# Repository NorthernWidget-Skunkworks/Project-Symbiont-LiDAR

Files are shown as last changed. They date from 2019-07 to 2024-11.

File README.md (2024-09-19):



# Project-Symbiont-LiDAR
Design files for a support and interface unit for the Garmin LiDAR Lite

Symbiosis

***The symbiont.*** *Lichens, like this Reindeer Lichen found in northeastern
Minnesota, are a symbiosis between fungi and algae. Our symbiosis is between
silicon, copper, aluminum, and laser. But be it nature or machine, some
partnerships are truly mutual in their benefits. Photo by Homer Edward Price.*

The [LiDAR Lite](https://buy.garmin.com/en-US/US/p/578152/pn/010-01722-10) is a rangefinder from Garmin capable of returning distances to objects up to 40 m away. It is an effective sensor for water, snow, and ice levels, among other purposes. Extensive work to characterize the LiDAR Lite for environmental sensing of water levels has been performed by:

Paul, J. D., Buytaert, W., & Sah, N.(2020). A technical evaluation of lidar-based measurement of riverwater levels. *Water Resources Research*, *56*, e2019WR026810. https://doi.org/10.1029/2019WR026810

## Technical specifications

### Electronic Hardware

* Microcontroller (computer) core
  * ATTiny1634
  * [Firmware](Firmware) written in Arduino-compatible C++
  * 12 MHz
* Sensors
  * Externally connected: [Garmin LiDAR Lite v3 HP](https://buy.garmin.com/en-US/US/p/578152/pn/010-01722-10)
  * On board
    * MEMS accelerometer to detect board angle
    * Hall-effect sensor to for user to trigger with a magnet after providing a known angle to the accelerometer. This corrects for offset errors in the accelerometer, significantly improving its angular accuracy.
* Connections and communications protocols
  * [LiDAR Lite v3 HP](https://buy.garmin.com/en-US/US/p/578152/pn/010-01722-10)
    * 6-pin screw-terminal header
    * Switchable 5V power supply
    * I2C
  * Data logger
    * Power in and Ground
    * Digital communications
      * I2C
* Power
  * Voltage limits: 3.3 ~ 5.5V
  * Power consumption: ~0.5mA @ 4.5V, take reading every 60 seconds, then power down
  * Power conditioning: Provides an onboard, high power, step up to 5V to allow for interface to 3.3V loggers
* Fault recovery: Using intermediate system to emulate an I2C connection prevents a global lockup of the logger system
* Status LED
* Open-source licensing via CC BY-SA 4.0

Symbiont board

### Electronic Software and Firmware

* Programmable using the Arduino IDE https://www.arduino.cc/en/main/software
* [Firmware](Firmware) available in this repository. At the time of writing, "LiDAR_InterfaceDemo" is the most up-to-date prototype firmware.
* [Software ](https://github.com/NorthernWidget-Skunkworks/Symbiont-LiDAR_Library) to use the Symbiont-LiDAR with Arduino-compatible devices
* Open-source licensing via GNU GPL 3.0

## Assembly

Rendered image of assembled LiDAR unit

Assembling this sensor is possible by hand with sufficient skill and the following tools:
* Temperature-controlled soldering iron
* Hot-air rework station
* Equipment for stenciling with solder paste
* ESD-safe tweezers and workstation
* Solder wick

Most of the components on this board are coarse enough in pitch that assembly by hand is expected to be relatively straightforward. However, if you are concerned about this, there are PCB assembly workshops located in many parts of the world.
>> THOUGHT: I have basic instructions for assembly on the [Project Walrus](https://github.com/NorthernWidget-Skunkworks/Project-TPDH-Walrus) README; I will not reproduce these here just yet, as we might want to set up a separate assembly guide, mostly with good links to existing resources, since our writing something of this nature would be to reinvent the wheel.

## Firmware

### Downloading and installing the Arduino IDE

Go to https://www.arduino.cc/en/main/software. Choose the proper IDE version for your computer. For Windows, we suggest the non-app version to have more control over Arduino; this might change in the future. You will have to add custom libraries, so the web version will not work (at least, as of the time of writing). Download and install the Arduino IDE. Open it to begin the next steps.

### AVR ISP

To install firmware on the Symbiont board, you use the [2x3-pin 6-pin ICSP (also called ISP) header](https://www.digikey.com/product-detail/en/3m/929665-09-03-I/3M156313-06-ND/681796) with a special device called an "in-circuit system programmer" (or just "in-system programmer; yup, that's what the acronym stands for).

Many devices exist to upload firmware, including:
* The official [AVR ISP mkII](http://ww1.microchip.com/downloads/en/DeviceDoc/Atmel-42093-AVR-ISP-mkII_UserGuide.pdf) (no longer produced but available used)
* Using an [Arduino as an ISP](https://www.arduino.cc/en/tutorial/arduinoISP)
* The versatile [Olimex AVR-ISP-MK2](https://www.olimex.com/Products/AVR/Programmers/AVR-ISP-MK2/open-source-hardware)
* The [Adafruit USBtinyISP](https://www.adafruit.com/product/46)

### Uploading the firmware

Using this ISP, upload (as of the time of writing): [the Arduino sketch in this folder](Firmware/AdditionalFirmware/LiDAR_Accelerometer_InterfaceDemo). To do so, follow these steps:

1. Open the Arduino IDE.
2. Follow [these instructions](https://github.com/SpenceKonde/ATTinyCore/blob/master/Installation.md) to install the [ATTinyCore board definitions](https://github.com/SpenceKonde/ATTinyCore)
3. Select [ATTiny1634](https://github.com/SpenceKonde/ATTinyCore/blob/master/avr/extras/ATtiny_1634.md) **(No bootloader)**
4. Plug your ISP of choice into your computer (via a USB cable) and onto the 6-pin header. There are two ways to place it on; the header is aligned such that the ribbon cable should be facing away from the board while programming. If this fails without being able to upload, try flipping the header around. This should both power the board and provide communications.
5. Go to Tools --> Programmer and select the appropriate programmer based on what you are using.
6. Go to Tools --> Burn Bootloader. Yes, we know that you just selected "ATTiny1634 (No bootloader)", but this step sets the fuses, which configure their internal oscillator and brown-out detection.
7. Go to Sketch --> Upload Using Programmer. After several seconds, you learn whether you succeeded or failed. Hopefully it worked!

Upload using programmer

***Uploading using the in-system programmer.***

***Important note for Linux users:*** You must supply permissions to the Arduino IDE for it to be able to use the ICSP, or you will have to run it using `sudo`. The former option is better; the latter is easier in the moment.

***Note: Be sure to download and/or update drivers for your ISP.***

## Writing a program to connect to the Symbiont-LiDAR

Once it is bootloaded and connected with a LiDAR Lite sensor, you should be able to use any standard Arduino device to connect to it and read its data.

### Very simple Arduino code

This code is intended for any generic Arduino system.

```c++
// Include the Symbiont library
#include "SymbiontLiDAR.h"

// Declare variables -- just as strings
String header;
String data;

// Instantiate class
SymbiontLiDAR myLaser;

void setup(){
    // Begin Serial connection to computer at 38400 baud
    Serial.begin(38400);
    // Obtain the header just once
    header = myLaser.getHeader();
    // Print the header to the serial monitor
    Serial.println(header);
}

void loop(){
    // Take one reading every (10 + time to take reading) seconds
    // and print it to the screen
    myLaser.updateMeasurements();
    data = myLaser.getString();
    Serial.println(data);
    delay(10000); // Wait 10 seconds before the next reading, inefficiently
}
```

### Northern Widget Margay code

The [Margay data logger](github.com/NorthernWidget-Skunkworks/Project-Margay) is the lightweight and low-power open-source data-logging option from Northern Widget. It saves data to a local SD card and includes on-board status measurements and a low-drift real-time clock. We have written [a library to interface with the Margay](github.com/NorthernWidget-Skunkworks/Margay_Library), which can in turn be used to link the Margay with sensors.

```c++
// Include the Symbiont library
#include "Margay.h"
#include "SymbiontLiDAR.h"

// Declare variables -- just as strings
// Empty header to start; will include sensor labels and information
String header = "";
String data;

// Instantiate classes
SymbiontLiDAR myLaser;
Margay Logger; // Margay v2.2; UPDATE CODE TO INDICATE THIS

// I2CVals for Symbiont
uint8_t I2CVals[] = {0x50}; // DEFAULT

//Number of seconds between readings
uint32_t updateRate = 60;

void setup(){
    header = header + myLaser.getHeader();
    Logger.begin(I2CVals, sizeof(I2CVals), header);
    initialize();
}

void loop(){
    Logger.run(update, updateRate);
}

String update() {
    initialize();
    return myLaser.getString();
}

void initialize(){
    myLaser.begin();
}
```

### Northern Widget Resnik code

>> Currently nearly identical to Margay code, by design. Add telemetry with Particle Boron.

```c++
// Include the Symbiont library
#include "Resnik.h"
#include "SymbiontLiDAR.h"

// Declare variables -- just as strings
// Empty header to start; will include sensor labels and information
String header;
String data;

// Instantiate classes
SymbiontLiDAR myLaser;
Resnik Logger;

// I2CVals for Symbiont
uint8_t I2CVals[] = {0x50}; // DEFAULT

//Number of seconds between readings
uint32_t updateRate = 60;

void setup(){
    header = header + myLaser.getHeader();
    Logger.begin(I2CVals, sizeof(I2CVals), header);
    initialize();
}

void loop(){
    Logger.run(update, updateRate);
}

String update() {
    initialize();
    return myLaser.getString();
}

void initialize(){
    myLaser.begin();
}
```

## Housing and cabling

### Parts required

This is what we used for our build; you can be creative based on materials and availability.

* Main enclosure
  * Polycase box [WC-20F (clear lid)](https://www.polycase.com/wc-20f)
  * [2x \#4 screws](https://www.polycase.com/screws-mbr-100) to mount Symbiont in box
  * Cable gland ([Heyco M4365](https://www.heyco.com/Liquid_Tight_Cordgrips/product.cfm?product=Liquid-Tight-Cordgrips-Metric&section=Liquid_Tight_Cordgrips)) for cable to LiDAR Lite
  * Strain-relieved cable gland ([Heyco M4425](https://www.heyco.com/Liquid_Tight_Cordgrips/product.cfm?product=Liquid-Tight-Cordgrips-Pigtail-Metric&section=Liquid_Tight_Cordgrips)) for cable to logger
  * Desiccant packs
* LiDAR Rangefinder and attachment to enclosure
  * [LiDAR Lite sensor](https://www.sparkfun.com/products/14599)
  * [4 sealing screws](https://www.mcmaster.com/90825A144/): \#4-40 x 3/8"
  * [4 washers](https://www.mcmaster.com/90107A005) for \#4 screws
  * [4 cap nuts](https://www.mcmaster.com/99022A101) for \#4-40 screws
* Mounting plate
  * Material: Acetal (Delrin) sheet: 1/4" thick. We commmonly use [12x24" black](https://www.eplastics.com/ACTLBLK0-25012X24); the black pigment increases its UV resistance
  * Rectangular dimensions for mount: 127 x 95.25 x 6.35 mm (5.00" x 3.75" x 0.25")
  * [Design](https://easel.inventables.com/projects/VMmCoOyJyiiKTospk1NBBQ) on Easel for X-carve (see also [CNC files here](CNC)). Note the 7 mm depth to ensure that the bit cuts all the way through the Acetal; use a piece of scrap material on your cutting bed if you want to protect it.
* Mounting plate fasteners
  * 1/4"-20 hardware to attach the box to the mounting plate
    * Bolts: [1" long; hex head convenient; zinc-plated medium-grade (Grade 5) recommended for lower price with good corrosion resistance](https://www.mcmaster.com/92865A542)
    * Nuts: [Zinc-plated Grade 5](https://www.mcmaster.com/95462A029)
    * Washers: Zinc-plated [SAE](https://www.mcmaster.com/90126A029) or [USS](https://www.mcmaster.com/90108A413)
    * Lock washers: We typically use [split-lock washers](https://www.mcmaster.com/zinc-plated-steel-washers/), but [tooth-lock washers](https://www.mcmaster.com/91113A029) are good for high-vibration environments.
  * 2 U bolts: 1/4"-20, inner diameter 3/4" to 1 3/4", to attach the mounting plate to a pipe. We typically mount this sensor on 3/4" pipe or conduit, and recommend a U bolt designed to fit this ([1/4"-20, 1 1/8" inner diameter](https://www.mcmaster.com/u-bolts/u-bolts-with-mounting-plates/for-pipe-size~3-4/)). Weather/corrosion resistance is helpful, especially if you are concerned about later removing the U bolts.
* Cable to logger
  * 3 m (or less) [4-conductor AlphaWire](https://www.digikey.com/product-detail/en/alpha-wire/5004C-SL001/5004CSL001-ND/484976), stripped and tinned at both ends. Other cables will work too; this is what we have found to be highest quality and reliability. We cannot guarantee successful I<sup>2</sup>C communications over cables longer than 3 meters.

Mounting plate perspective view in Easel

***Mounting plate perspective view in [Easel](https://easel.inventables.com/projects/VMmCoOyJyiiKTospk1NBBQ)*** *for easy integration with the X-carve series of lower cost CNC routers.*

### Assembly

Prior to assembly, ensure that you have:
* [Uploaded the firmware to the Symbiont board](#Uploading-the-firmware)
* Fabricated [the mounting plate](CNC) (see also the [Easel online CNC setup](https://easel.inventables.com/projects/VMmCoOyJyiiKTospk1NBBQ)) if desired.

1. Drill and tap 12 mm holes in the side of the box. Use a M12-1.5 tap for the threads.

2. Install the Symbiont board as shown below using two of the \#4 self-tapping screws.

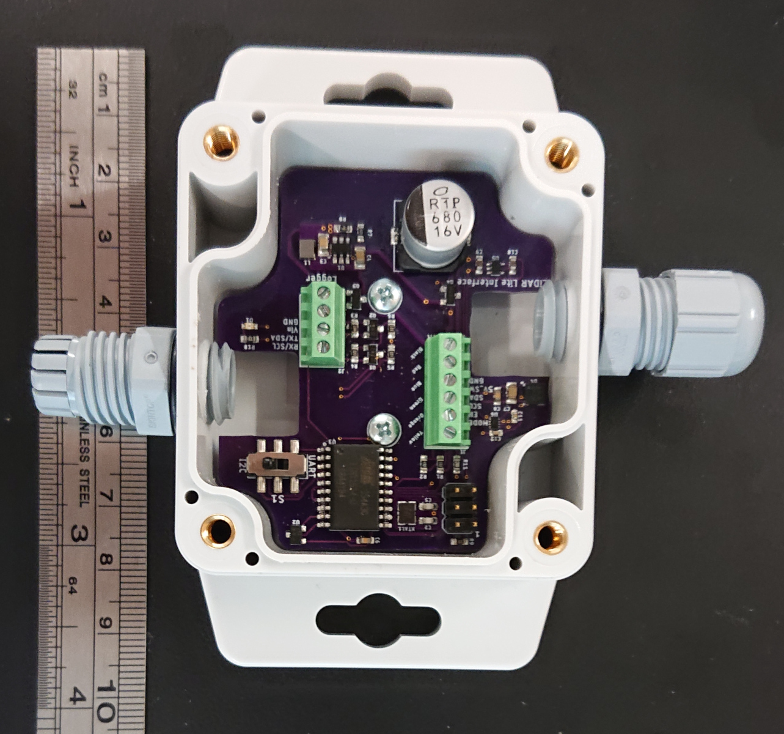
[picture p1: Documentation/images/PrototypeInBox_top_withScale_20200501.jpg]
Symbiont prototype in box


3. Using the sealing screws, cap nuts, and washers, install the LiDAR Lite sensor onto the lid. By mounting the LiDAR Lite at an angle, you can fix it to the box lid in a way that still allows the box to open and close properly. The cap nuts go on the outside of the housing.

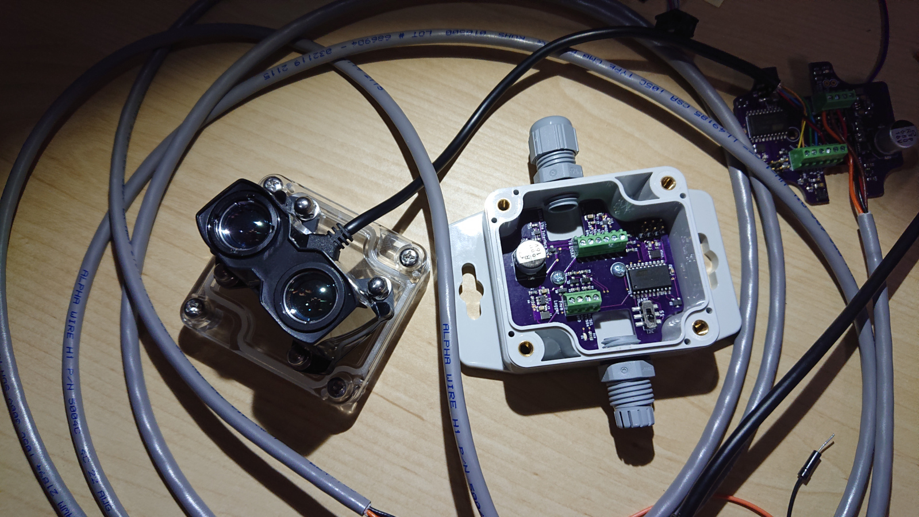
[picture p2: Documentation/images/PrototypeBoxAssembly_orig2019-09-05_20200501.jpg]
Prototype sensor assembly


4. Thread the cables through the cable glands and attach them to the screw terminals. A 1.8 mm flat-head screwdriver can be very useful for this. Note that these cables cross the board in the above image (upper left) -- and that (unlike in the image!) you should do this *after* the board is in the box.

5. Using the switch in the box, select the desired communications protocol. For most of our uses, this is I2C.

6. Attach the cable to the data logger.

7. Test the LiDAR Lite unit.

8. When satisfied with the tests, turn off the data logger and place a protective cover over the lenses of the LiDAR Lite for safety during transport. We have [a set of "safety glasses" available for 3D printing](3Dprint). You may want to secure these in place with electrical tape.

9. Place desiccant in the box. I typically install two small desiccant packs on the side of the board above the switch and large capacitor and pack them in so they are unlikely to move; this is in order to keep the indicator LED visible.

10. Securely screw the lid onto the box to seal the LiDAR Lite + Symbiont unit.

11. Mark the corner of the box next to the Hall-effect sensor, and mark the orientations of the roll and pitch axes. The pitch axis should be positive when the long strain-relieved cable gland tilts upwards. The roll axis should be positive when, when looking at the side of the assembly such that the long strain-relieved cable gland is on the left and the laser rangefinder is pointed up, the laser rangefinder rolls towards you.

Side view: long axis, with pitch +/- marked

Side view: short axis, LiDAR Lite cable, with roll +/- marked

>> Add an annotated picture of Hall-Effect sensor location

12. Place the box on a measured flat surface and tap the magnet to the marked location by the Hall Effect sensor. This will appropriately zero the offsets for the sensor and increase its near-horizontal accuracy significantly. This must be done when the sensor is powered; the LED will light up during the full duration of magnetic contact. When connected to a logger, this can be done by putting the magnet in place, hitting the "RESET" button (e.g., on a Margay logger), and then holding the magnet in place with the read light on until the first reading is complete. Doing this while connected to a computer is recommended in order to see the first reading on the serial monitor and double check that the zeroing/calibration is appropriate. For a convenient magnet holder, you can use our [3D-printable magnetic wand][3Dprint], which holds a small rare-Earth magnet. This may be a generic part, though this [3/8" x 1/8" Neodymium Disk Magnet](https://www.apexmagnets.com/magnets/3-8-x-1-8-disc-neodymium-magnet) works well in our experience.

13. Use the 1/4"-20 hardware to attach the LiDAR Lite box to the mounting plate. The bolts pass through the center holes on the tabs on either side of the box, with their heads towards the box lids.

>> Note: Mounting plate holes currently too small for these; will need to be updated. Currently using #8 hardware. Figures for pitch+roll have 1/4-20 -- I probably drilled it out wider for these.

14. (Can wait for field installation) attach the unit via its mounting plate to the appropriate pipe, post, etc. This typically involves the U bolts, noted above. Curved EMT conduit can be helpful for providing a way to select the angle of the sensor. Although we use a single 45-degree bend piece of conduit in the images below, we might suggest attaching a 90-degree bend conduit first, and then a 45-degree bend as necessary to adjust the sensor away from a direct down-looking view; the sensor will attach directly to the convex side of the bend instead of bridging over airspace, which required us to use rocks as shims to reduce mounting-plate flexure. (This suggestion, however, increases torque on the mast; future field testing is needed to determine the best method.) ***Note: The LiDAR Lite unit will likely give a return only if its angle to the surface that it is measuring is steeper (i.e., more orthogonal) than 45 degrees.***

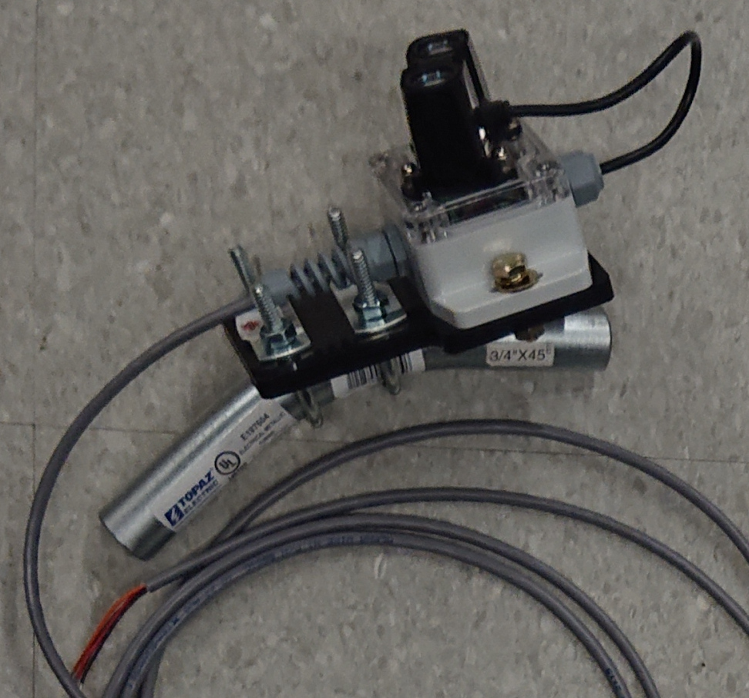
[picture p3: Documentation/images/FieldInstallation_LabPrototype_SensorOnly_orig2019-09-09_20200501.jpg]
Field installation prototype in the lab: Sensor only


## Field installation

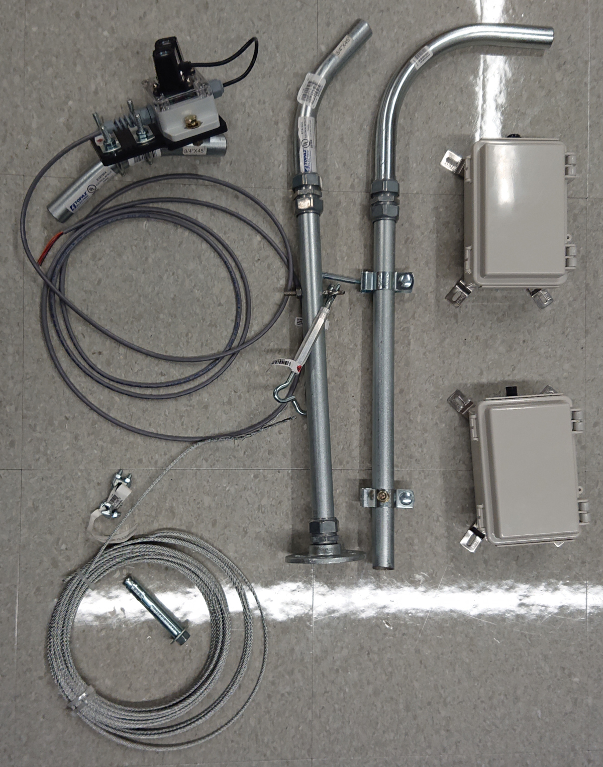
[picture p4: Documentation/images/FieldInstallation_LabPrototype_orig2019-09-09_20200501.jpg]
Field installation prototype in the lab


***Lab mock-up of field installation for LiDAR Lite.*** *The boxes at right contain [Northern Widget Margay](https://github.com/NorthernWidget-Skunkworks/Project-Margay) data loggers with a single cable gland to connect to the Symbiont box. The two posts next to them provide examples of how to connect the 3/4" EMT conduit to some fixed point in the environment, either the side of a flat(ish) wall (right) -- though the brackets aren't necessary or even always good, since we can bolt right through the pipe -- or to a flat(ish) surface using a floor flange. We drilled holes through the conduit to attach 1/4" eye bolts (1/4"-20, 1.5" long) using nuts, lock washers, and washers, to the conduit. These eye bolts then held turnbuckles to which we attached cables (lower left). The other end of the cables can be attached via sleeve or wedge anchors to rock, or to other sturdy structures. The LiDAR Lite + Symbiont is in the upper left corner, albeit attached in a way that would have it looking up... unless it were attached to the end of the 90-degree bend.*

### Mast construction

#### Supplies

* 3/4" EMT rigid conduit
  * Straight: main mast
  * 90-degree bend
  * 45-degree bend
* 3/4" Conduit screw-down connectors (to join multiple pieces of conduit)
* 3/4" Conduit-to-threaded connectors (to link smooth conduit to threaded 3/4" plumbing, needed only if you use a floor flange)
* Floor flange (1, if you want to attach to a flat surface)
* 1/4-20 x 1.5" eye bolts (3, +1 in case you bend/break one)
* 1/4" x 2+" long sleeve or wedge anchors; 4 for the floor flange or 2 for bolting into the side of a rock. Extras suggested, as these can be broken during installation.
* Turnbuckles; I suggest getting 3 that are threaded all the way down (as shown in the picture above). Get an extra in case you break one.
* 1/8" metal cable
* 1/8" cable clamps (x6, +1 in case you lose the nuts)
* 1/8" metal cable turns (x6; if you lose one, don't worry; these are nice for durability but not totally necessary)
* 3/8" x 2.5+" long sleeve or wedge anchors for the cables; these are less breakable than their 1/4" cousins, but you might still want an extra one.
* Extra 1/4"-20 hardware. I almost always end up needing this.
* Cable management (keep secure and prevent from flapping in the wind, which can cause damage)
  * Cable ties (zip ties). Ensure that these are UV-resistant; many black ones are.
  * Electrical tape
* *Optional:* 2x ~1-3/4" hose clamps if mounting a data-logger box for the [Margay](https://github.com/NorthernWidget-Skunkworks/Project-Margay) on the main mast. Longer hose clamps (or multiple 1-3/4" clamps in series) for larger logger boxes, so long as they can remain stable on the mast.

You might not need the guy wires and associated hardware if you bolt your assembly to the side of something (like a rock or wall). Some guy wires are generally encouraged.

#### Assembly

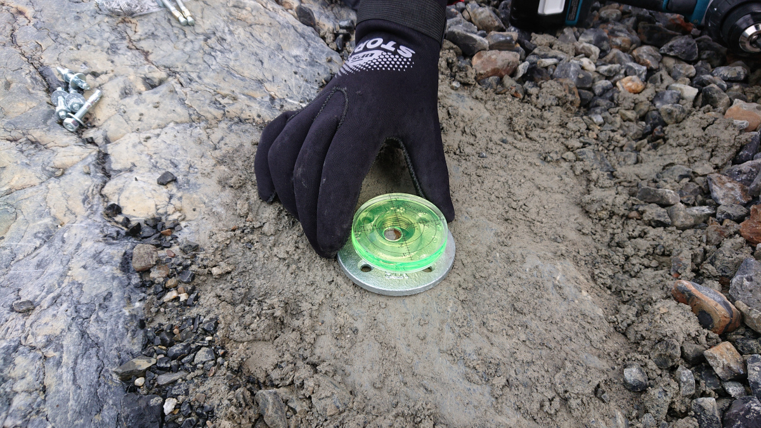
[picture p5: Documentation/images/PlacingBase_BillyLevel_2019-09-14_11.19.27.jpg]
Leveling the base

***Placing and leveling the base.***

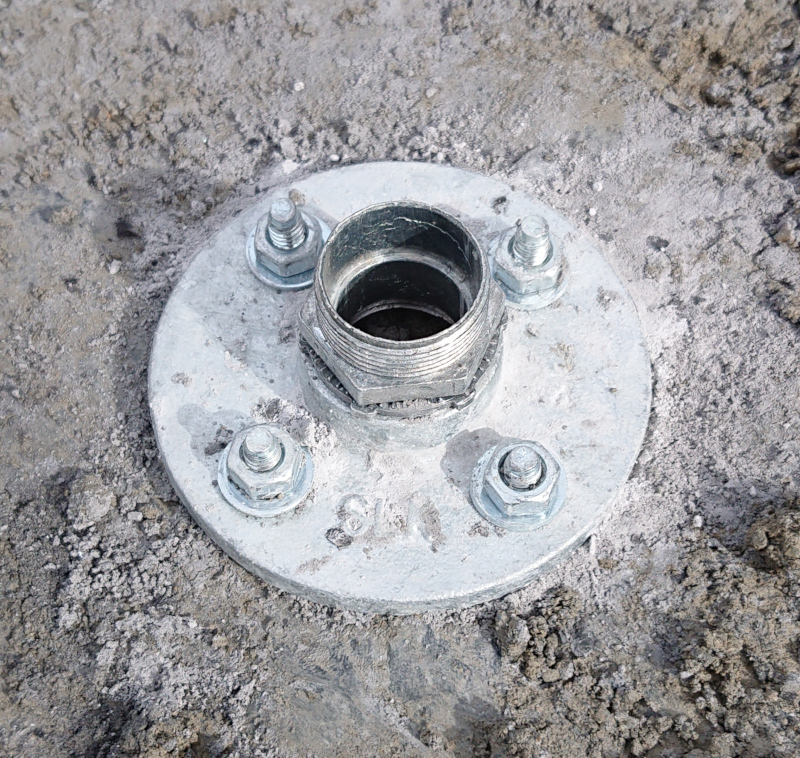
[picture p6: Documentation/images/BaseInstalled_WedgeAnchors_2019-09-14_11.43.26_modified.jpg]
Base is installed using wedge anchors

***Installing the base using wedge anchors.***

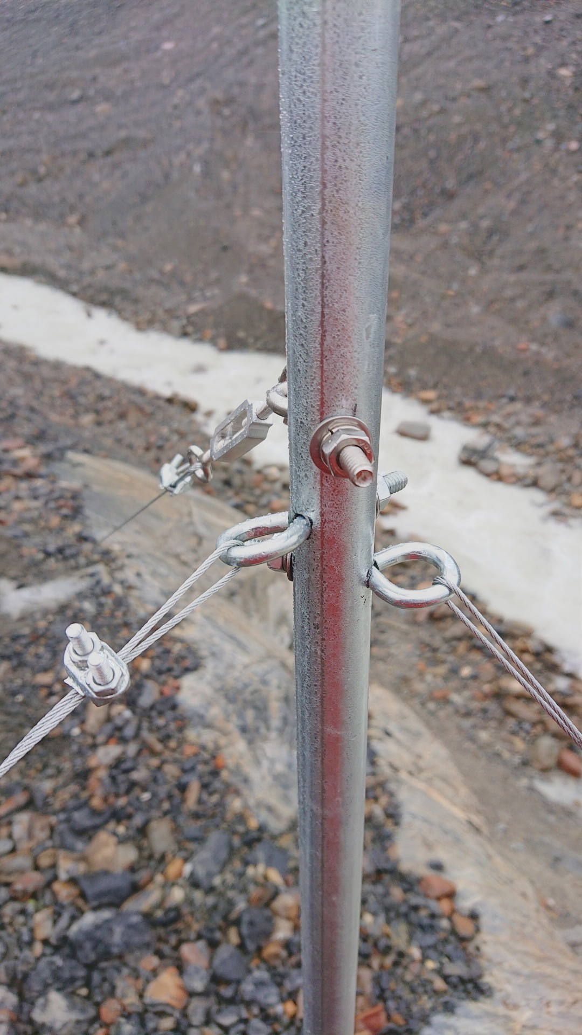
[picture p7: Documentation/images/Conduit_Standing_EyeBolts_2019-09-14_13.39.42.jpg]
Conduit installed and anchored with eye bolts and turbuckles.

***Installing the conduit and anchoring it with eye bolts and turnbuckles.*** *Before going out to the field, we strongly suggest you pre-drill the holes and pre-install the eye bolts.*

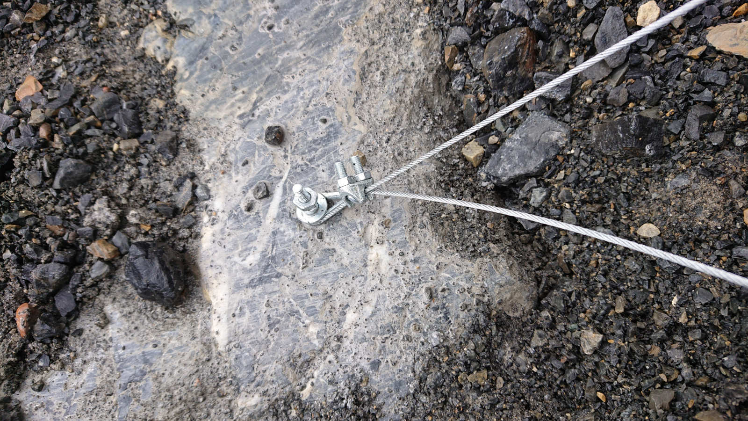
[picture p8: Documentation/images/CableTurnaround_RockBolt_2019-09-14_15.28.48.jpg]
Cable to rock bolt

***Tightening the cable around the bolt in the rock using the cable clamp.***

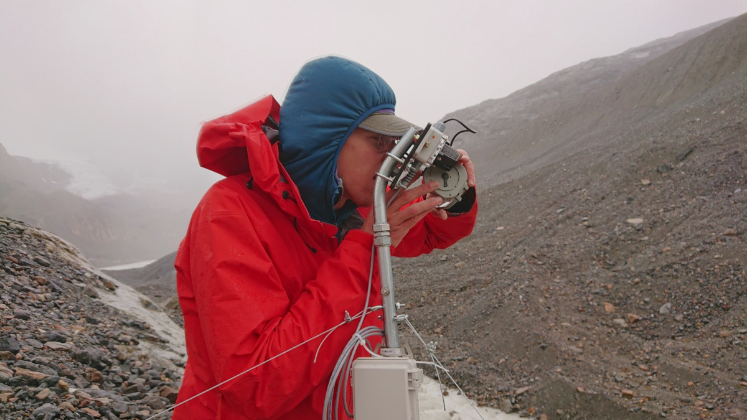
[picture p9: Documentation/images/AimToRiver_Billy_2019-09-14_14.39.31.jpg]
Aiming the LiDAR Lite

***Aiming the LiDAR Lite unit at the river.*** *In future models, we are considering adding peep sights to the mounting bracket. [Professor Billy Armstrong](https://earth.appstate.edu/faculty-staff/dr-william-h-armstrong) in the photo.*

The quality of any zeroing with the Hall-effect sensor will be limited by the ~1-degree precision of the accelerometer that is used as an inclinometer; as an additional check, it is recommended to measure and record the orientation of the field-mounted unit by hand.

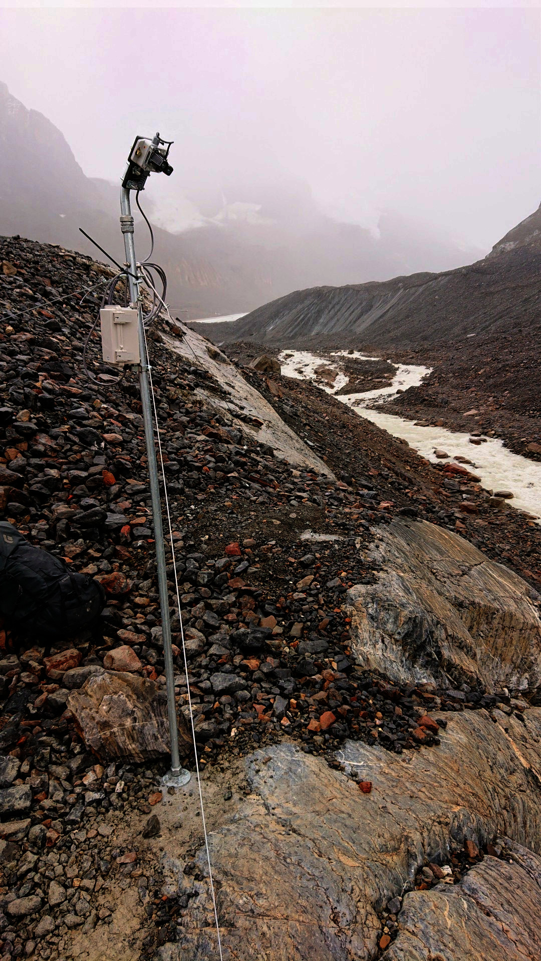
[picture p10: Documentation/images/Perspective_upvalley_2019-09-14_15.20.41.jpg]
Perspective view upvalley

***Fully installed clifftop unit***

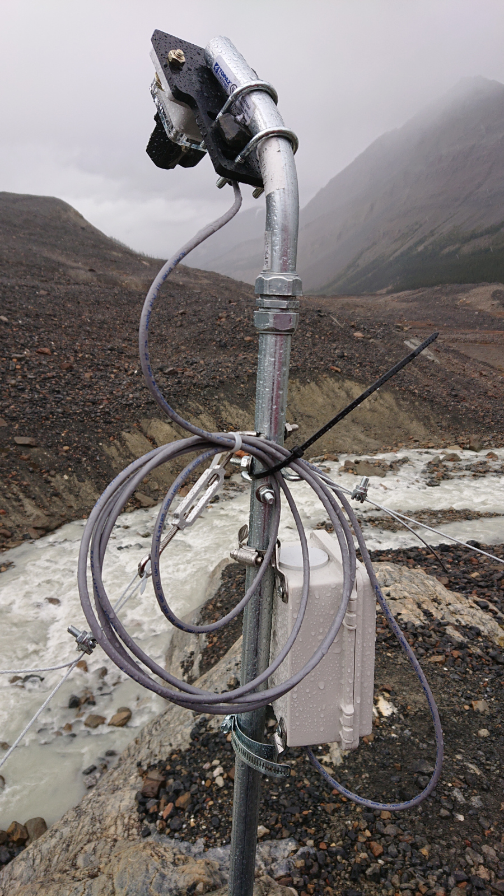
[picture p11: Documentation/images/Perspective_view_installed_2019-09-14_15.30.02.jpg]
Perspective view after installation.

***Fully installed clifftop unit*** *Note data-logger box attached with cable ties, as well as the mounting-plate attachment. For the latter, we used a rock as a shim with a 45-degree piece of EMS conduit. However, it may have been better to use a 90-degree piece of conduit and a 45-degree piece of conduit together to keep us from needing this shim -- though this would have increased torque on the main mast.*

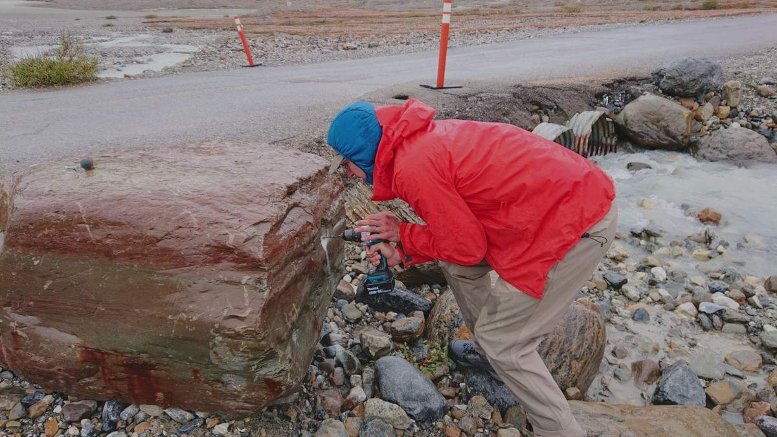
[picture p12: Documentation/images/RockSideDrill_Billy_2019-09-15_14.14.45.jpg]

***Alternative method: installing on the side of a rock.***

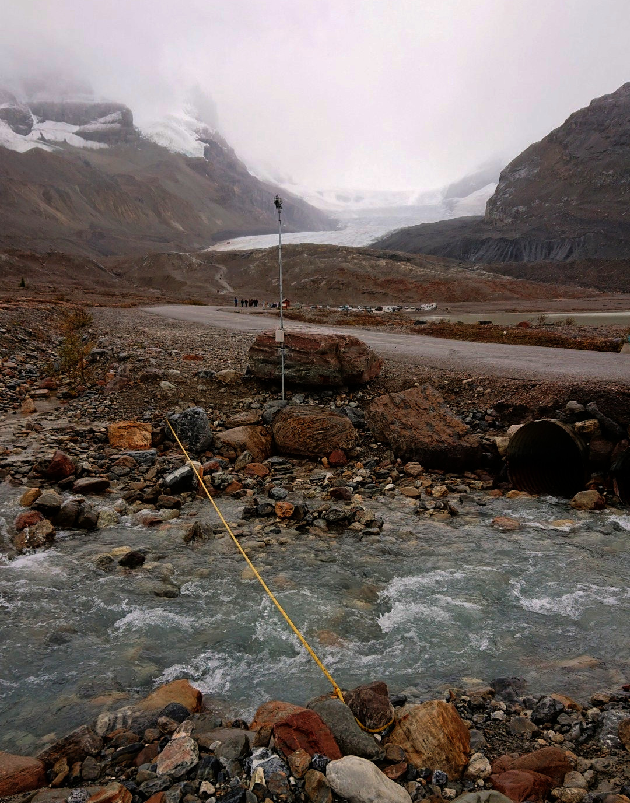
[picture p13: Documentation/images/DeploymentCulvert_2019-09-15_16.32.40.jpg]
Culvert deployment with context

***Full mast installed on the side of a rock.*** *Note the LiDAR Lite + Symbiont and the data-logger box.

## Acknowledgments

Support for this project provided by:

UMN ESCI

WMO

<br/>
<br/>
<br />This work is licensed under a <a rel="license" href="http://creativecommons.org/licenses/by-sa/4.0/">Creative Commons Attribution-ShareAlike 4.0 International License</a>.

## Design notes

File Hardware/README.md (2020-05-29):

 `LiDAR_Lite_Interface_HardSwitch`
- A expanded version of `LiDAR_Lite_Interface`
- Adds accelerometer 
- Uses physical switch to toggle between UART and I2C communication (as opposed to being firmware controlled in `LiDAR_Lite_Interface` and `LiDAR_Lite_Interface_CAN`
- Adds power switch to disconnect LiDAR Lite 
- Adds hall effect switch to trigger auto-level or other operation

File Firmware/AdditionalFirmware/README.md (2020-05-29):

* `LiDAR_Accelerometer_InterfaceDemo.ino` does not have full control functionality for the LiDAR Lite or the hall effect sensor.
* `HallEffect_Tester.ino` is simply a demo script to test magnet strength and area of effect most easily.

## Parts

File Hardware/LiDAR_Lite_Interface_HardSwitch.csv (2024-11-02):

Qty | Value | Device | Package | Parts | Description | DIGIKEY | DISP | MF | MPN | VALUE | VALUE_PART
1 |  | ATTINY1634SOIC | SO-20DW | U3 | ATtiny1634 8 bit AVR Microcontroller | ATTINY1634-SURCT-ND |  | Atmel | ATTINY1634-SUR
1 |  | CONN_02 | 1X02 | J3 | Genaric 2 terminal header
2 | 0.1uF | C-EU0.1UFC0402 | C0402 | C11, C12 | CAPACITOR, European symbol | 490-4759-1-ND |  | Murata | GCM155R71C104KA55D
3 | 0.1uF | C-EU0.1UFC0603 | C0603 | C6, C8, C13 | CAPACITOR, European symbol | 490-6051-1-ND |  | Murata | GCM188R71E104KA57D
1 | 1.62M | R-EU_1.62MR0603 | R0603 | R7 | RESISTOR, European symbol | RMCF0603FT1M62CT-ND |  | Stackpole | RMCF0603FT1M62 |  | 1.62M
1 | 1.8k | R-EU_1.8KR0603 | R0603 | R13 | RESISTOR, European symbol | 311-1.80KHRCT-ND |  | Yageo | RC0603FR-071K8L |  | 1.8k
6 | 10k | R-EU_10KR0603 | R0603 | R3, R4, R5, R6, R9, R14 | RESISTOR, European symbol | 311-10.0KHRCT-ND |  | Yageo | RC0603FR-0710KL |  | 10k
2 | 10pF | C-EU10PFC0603 | C0603 | C2, C5 | CAPACITOR, European symbol | 311-1058-1-ND |  | Yageo | CC0603JRNPO9BN100CC0603JRNPO9BN100
3 | 10uF | C-EU10UFC0805 | C0805 | C3, C4, C7 | CAPACITOR, European symbol | 490-6473-6-ND |  | Murata | GRM21BR61C106KE15K
1 | 180k | R-EU_180KR0603 | R0603 | R8 | RESISTOR, European symbol | P180KHCT-ND |  | Panasonic | ERJ-3EKF1803V |  | 180k
1 | 1k | R-EU_1KR0603 | R0603 | R11 | RESISTOR, European symbol | 311-1KLDCT-ND |  | Yageo | AC0603FR-071KL |  | 1k
2 | 1uF | C-EU1UFC0603 | C0603 | C9, C10 | CAPACITOR, European symbol | 490-10479-1-ND |  | Murata | GRM188R61C105KA12D
1 | 2.2k | R-EU_2.2KR0603 | R0603 | R12 | RESISTOR, European symbol | 311-2.20KHRCT-ND |  | Yageo | RC0603FR-072K2L |  | 2.2k
2 | 330 | R-EU_330R0603 | R0603 | R10, R15 | RESISTOR, European symbol | 311-330HRCT-ND |  | Yageo | RC0603FR-07330RL |  | 330
2 | 4.7k | R-EU_4.7KR0603 | R0603 | R1, R2 | RESISTOR, European symbol | 311-4.70KHRCT-ND |  | Yageo | RC0603FR-074K7L |  | 4.7k
1 | 6.8uH | INDUCTOR1008 | 1008 | L1 | Genaric inductor | 732-4849-1-ND |  | Wurth | 74438323068
1 | 680uF | CPOL-EUUW-10X10 | UW-10X10_NICHICON | C1 | POLARIZED CAPACITOR, European symbol | 493-2182-1-ND |  | Nichicon | UWT1C681MNL1GS
1 | AVRISP-6 | AVRISP-6 | AVRISP | ISP1 | AVR ISP HEADER
1 | CONN_42.54_SCREW | CONN_42.54_SCREW | 1X04_SCREW | J2 | Genaric 4 terminal header | ED10563-ND |  | On Shore | OSTVN04A150
1 | CONN_6SCREW_2.54 | CONN_6SCREW_2.54 | 1X06_SCREW | J1 | Genaric 6 terminal header | ED10565-ND |  | OnShore | OSTVN06A150
1 | CRYSTAL_SHIELD3.2X2.5 | CRYSTAL_SHIELD3.2X2.5 | CRYSTAL_3.2X2.5_4-SMD | XTAL1 | Crystal Oscilator w/Shield | 535-10901-1-ND |  | Abricon | ABM8G-12.000MHZ-4Y-T3
1 | DMG3404 | MOSFET-NCH-DMG3404L | SOT23-3 | Q3 | N-channel MOSFETs | DMG3404L-7DICT-ND |  | Diodes Incorporated | DMG3404L-7 | DMG3404
1 | JUMPER-SMT_2_NC_PASTE_SILK | JUMPER-SMT_2_NC_PASTE_SILK | SMT-JUMPER_2_NC_PASTE_SILK | JP1 | Normally closed solder jumper
1 | LED0603 | LED0603 | LED_0603 | D1 | Genaric LED | 732-4978-1-ND |  | Wurth | 150060RS75000
1 | LIS3DHLGA | LIS3DHLGA | LGA-16 | U4 | LIS3DH - Ultra-low-power High-performance 3-axis Digital Accelerometer (I2C/SPI) | 497-10613-1-ND |  | ST | LIS3DHTR
1 | MIC2544MSOP | MIC2544MSOP | MSOP_8 | U7 | MIC2544/48 - Hight Side Load Switch, with Adjustable Current Limit | 576-1738-5-ND |  | Microchip | MIC2544-1YMM
1 | MIC53653.3SC70 | MIC53653.3SC70 | DCK_R-PDSO-G5 | U5 | MIC5365-* - Low Power, High Performance, Linear Regulator | 576-3193-1-ND |  | Microchip | MIC5365-3.3YC5-TR
2 | MOSFET-NCH-2N7002P | MOSFET-NCH-2N7002P | SOT23-3 | Q1, Q2 | N-channel MOSFETs | 1727-4692-1-ND |  | Nexperia | 2N7002P | 215
1 | SWITCH_DPDTJS_GULLWING | SWITCH_DPDTJS_GULLWING | JS202011SCQN | S1 | Genric DPDT Switch | 401-2002-1-ND |  | C&K | JS202011SCQN
1 | TCS40DPRSOT23 | TCS40DPRSOT23 | SOT23-3 | U2 | Hall Effect Sensor (TCS40DPR) | TCS40DPRLFCT-ND | TCS40DPR | Toshiba | TCS40DPR | LF
1 | TLV61220DBV | TLV61220DBV | DBV_R-PDSO-G6 | U1 | TLV61220 - Low-Input Voltage Step-Up Converter (Boost) | 296-30547-1-ND |  | TI | TLV61220DBVR
1 | TXS0102DQM | TXS0102DQM | DQM_R-PX2SON-N8 | U6 | TXS0102 - 2 Channel Bidirectional Voltage Level Translator | 296-28435-1-ND |  | TI | TXS0102DQMR

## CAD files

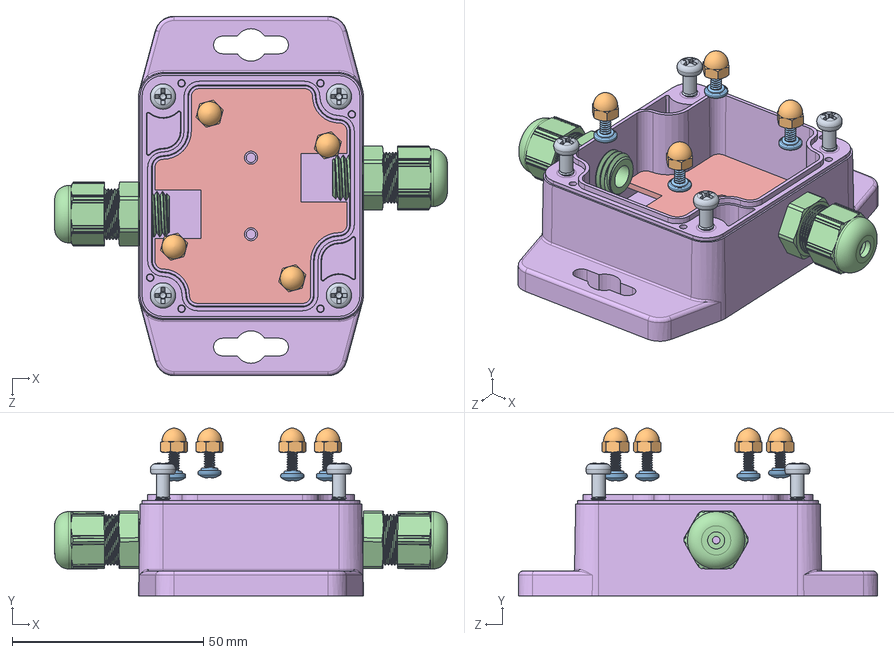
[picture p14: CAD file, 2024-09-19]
Mechanical/Box/Full.SLDASM
102.8 x 43.9 x 94.0 mm
WC-20F_Body_NOTHREAD
PCB
7310K51_Plastic Submersible Cord Grip_NONUT x 2
90825A142_Sealing Pan Head Screws x 4
99022A101_18-8 Stainless Steel Cap Nut x 4
WC-20F_Screw x 4

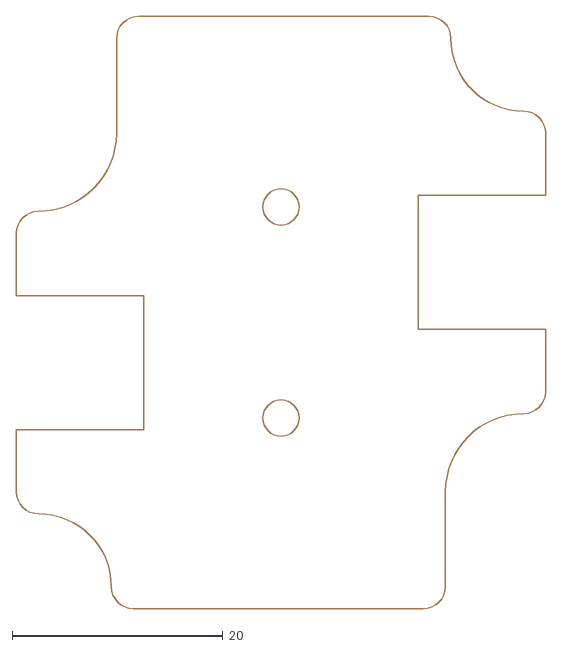
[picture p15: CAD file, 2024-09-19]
Hardware/LiDAR_Lite_Interface_HardSwitch.dxf
50.2 x 56.2

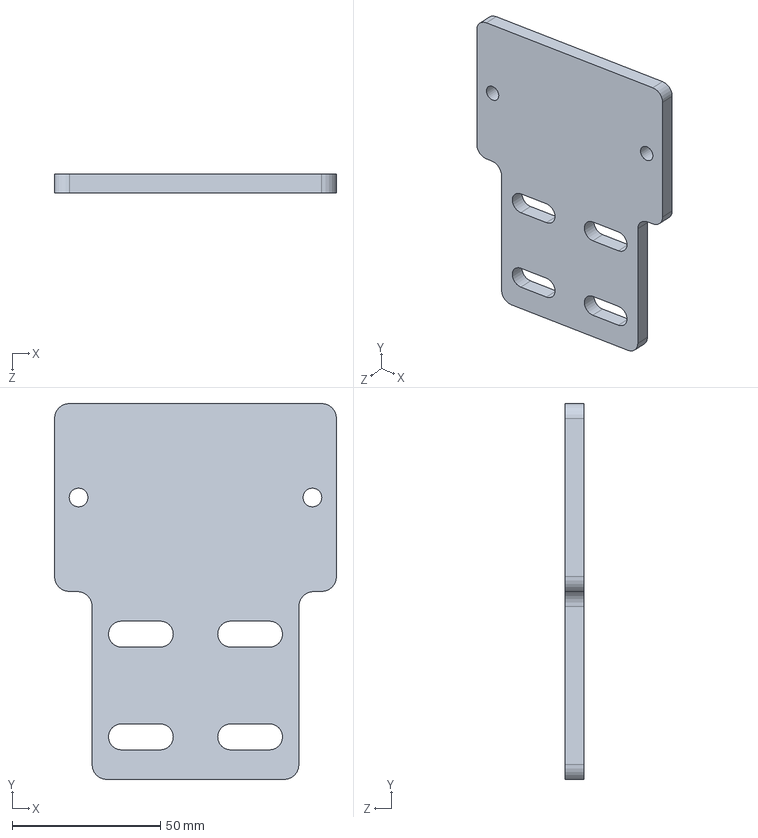
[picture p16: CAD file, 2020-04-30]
CNC/LiDARLite_Symbiont.SLDPRT
95.2 x 127.0 x 6.35 mm

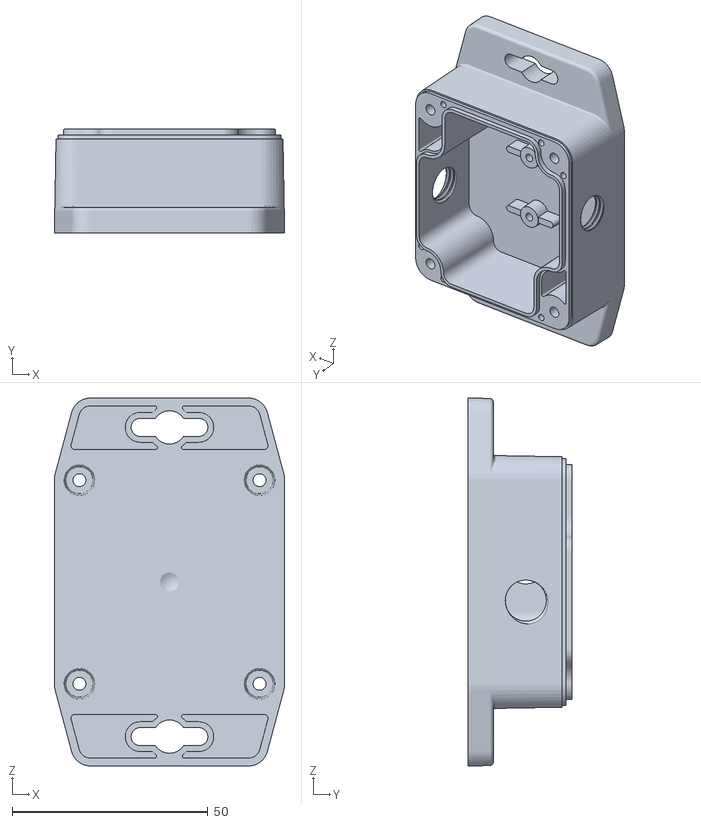
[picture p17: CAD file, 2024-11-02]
Mechanical/Box/WC-20F_Body_THREADED.STL
58.8 x 26.5 x 94.0

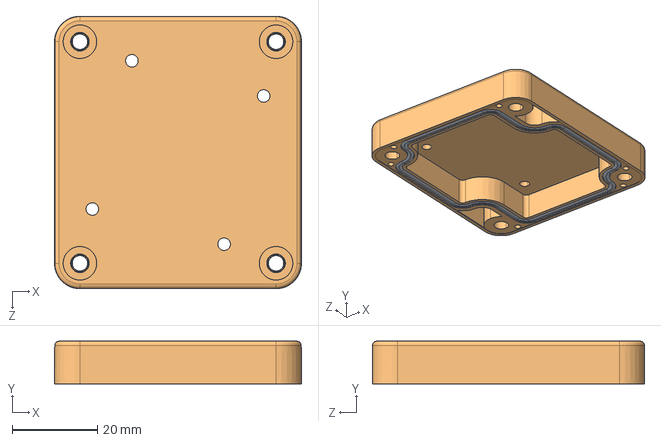
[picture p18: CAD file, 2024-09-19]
Mechanical/Box/WC-20F_Lid.STEP
58.0 x 10.0 x 63.9 mm

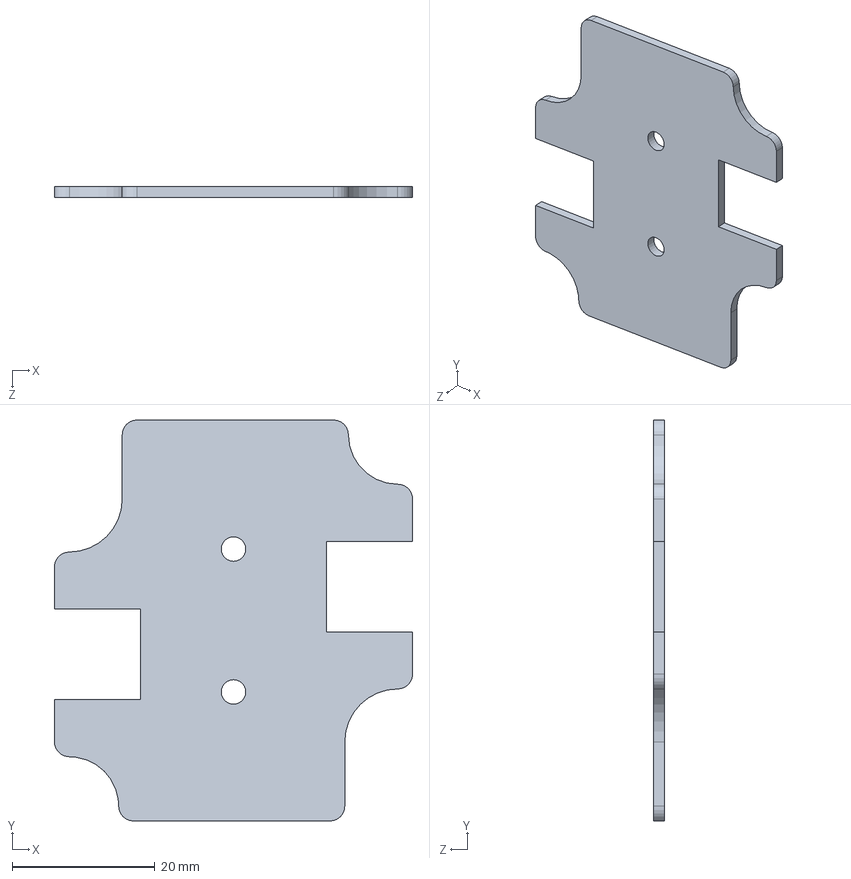
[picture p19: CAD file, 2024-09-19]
Mechanical/Box/PCB.SLDPRT
50.2 x 56.2 x 1.60 mm

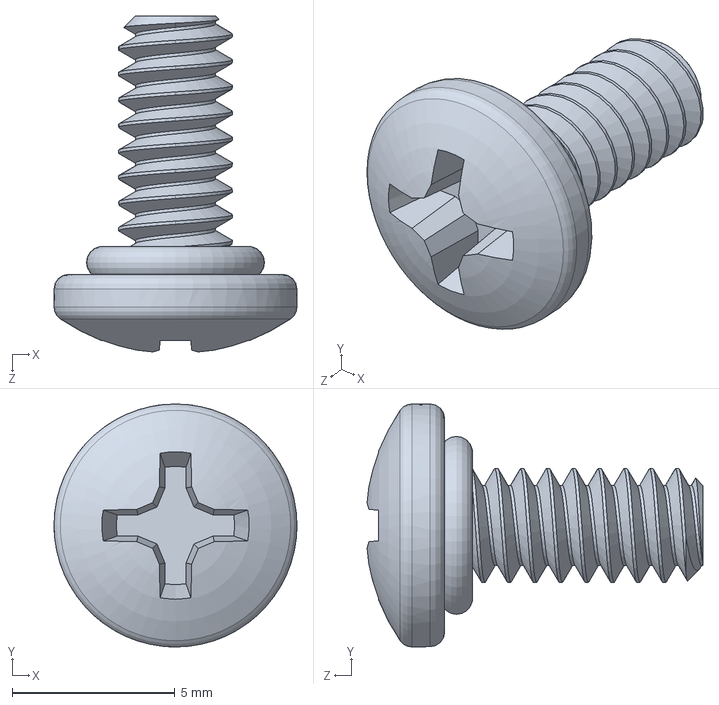
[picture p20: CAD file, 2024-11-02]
Mechanical/Box/90825A162_Sealing Pan Head Screws.SLDPRT
7.47 x 7.47 x 10.3 mm

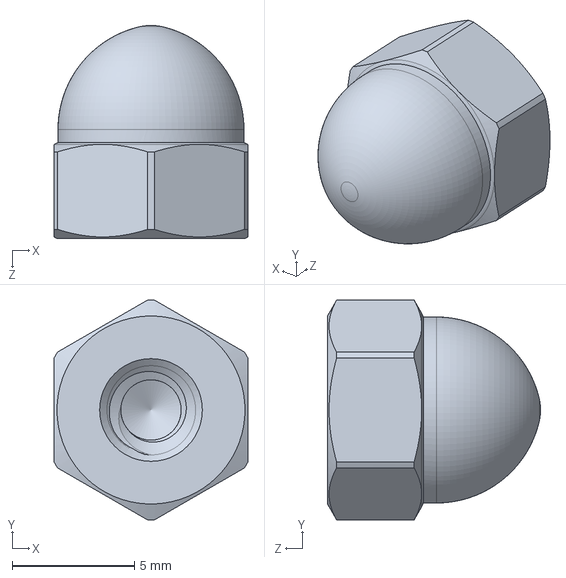
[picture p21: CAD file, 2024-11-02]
Mechanical/Box/91855A430_18-8 Stainless Steel Cap Nut.SLDPRT
7.94 x 9.01 x 8.73 mm

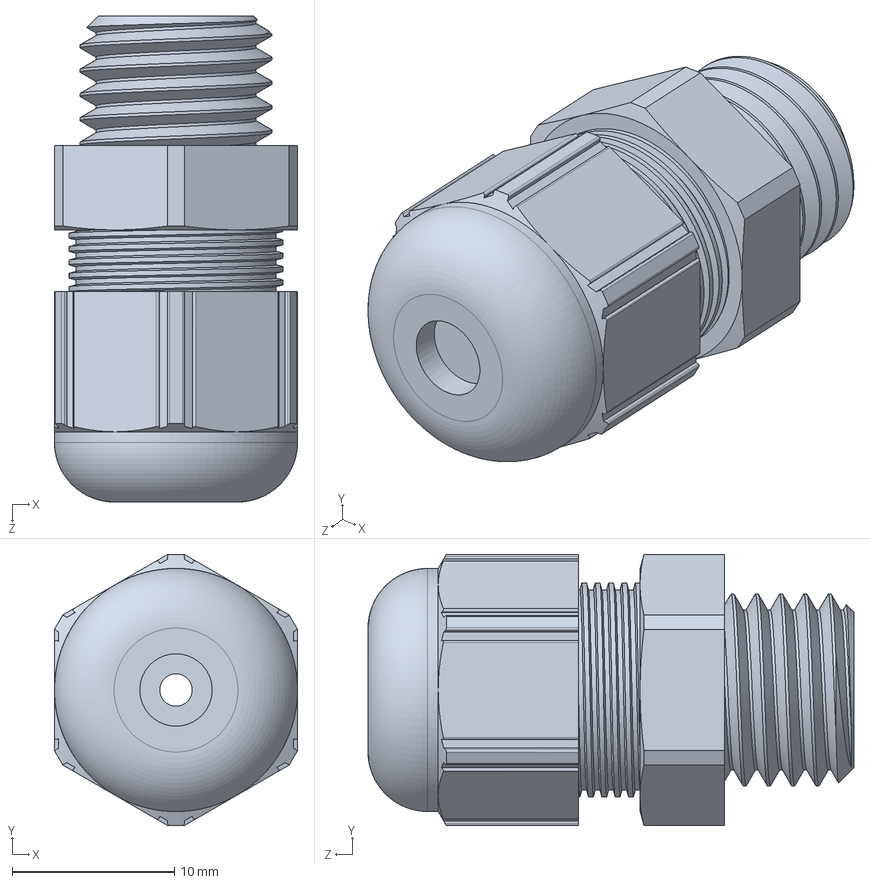
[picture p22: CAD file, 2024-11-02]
Mechanical/Box/7310K51_Plastic Submersible Cord Grip_NONUT.SLDPRT
15.0 x 16.7 x 30.0 mm

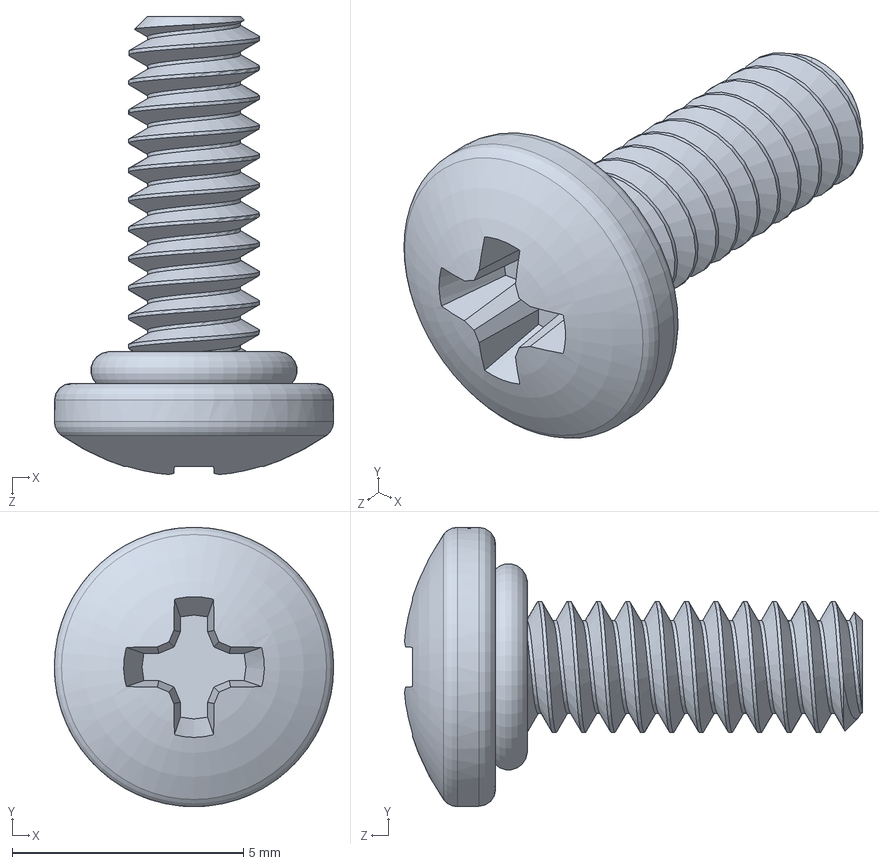
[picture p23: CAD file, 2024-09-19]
Mechanical/Box/90825A142_Sealing Pan Head Screws.SLDPRT
6.05 x 6.05 x 9.91 mm

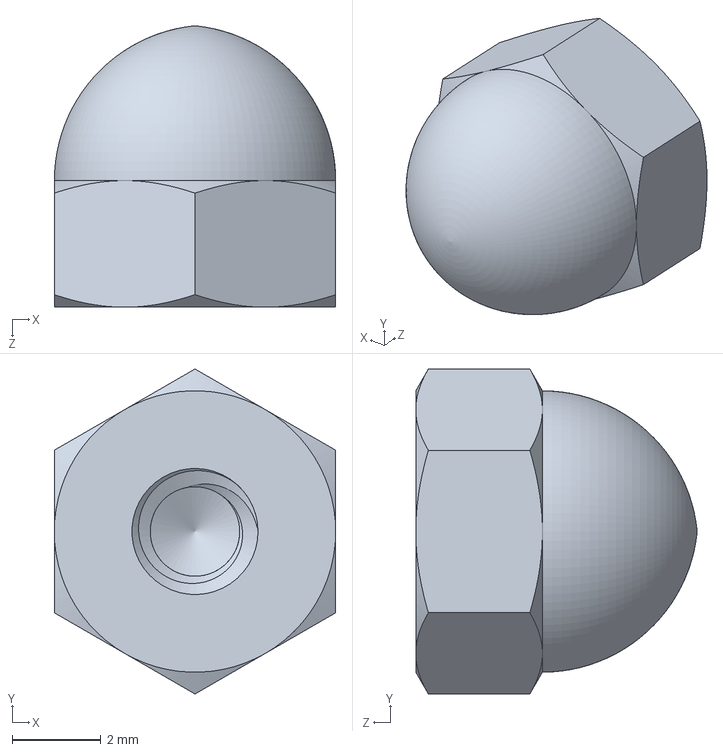
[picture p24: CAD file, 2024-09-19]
Mechanical/Box/99022A101_18-8 Stainless Steel Cap Nut.SLDPRT
6.35 x 7.33 x 6.35 mm

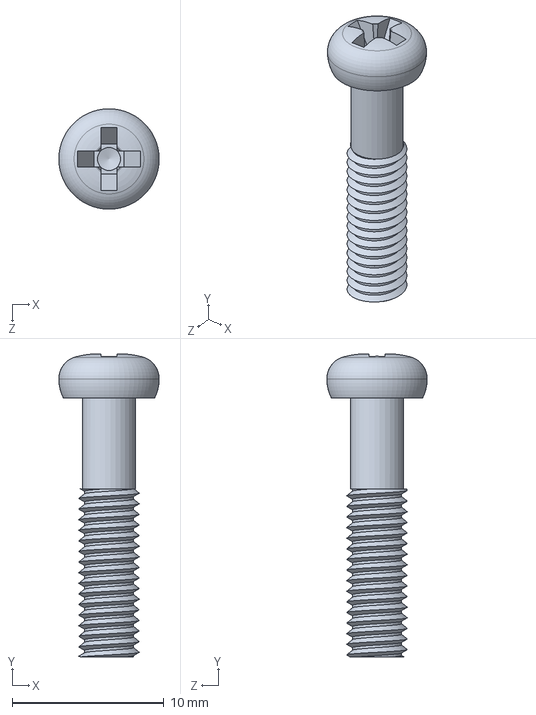
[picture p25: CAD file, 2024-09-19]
Mechanical/Box/WC-20F_Screw.SLDPRT
6.63 x 20.0 x 6.63 mm

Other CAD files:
3Dprint/MagnetWand.SLDPRT
CNC/LiDARLite_Symbiont_Mount.DXF
3Dprint/LiDARLiteCover.SLDPRT
3Dprint/LidarLitePlate.SLDPRT
Mechanical/Box/WC-20F_Body.STEP
Mechanical/Box/WC-20F_Body_NOTHREAD.SLDPRT
3Dprint/LiDARLiteCover.STL
3Dprint/LidarLitePlate.STL
3Dprint/MagnetWand.STL
Mechanical/Box/97349A415_Rounded Head Thread-Forming Screws.SLDPRT
Mechanical/Box/WC-20F_Body.SLDDRW
Mechanical/Box/WC-20F_Body.SLDPRT
Mechanical/Box/WC-20F_Lid.SLDDRW
Mechanical/Box/WC-20F_Lid.SLDPRT
Mechanical/Box/WC-20F_Lid.STL
Mechanical/Garmin LIDAR-Lite V3HP.SLDDRW
Mechanical/LIDAR-Lite_v3.SLDDRW

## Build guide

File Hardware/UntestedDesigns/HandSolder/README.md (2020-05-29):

`LiDAR_Lite_Interface_CAN`
- Unfinished minor variant of `LiDAR_Lite_Interface`
- Uses can type crystal with tabs for `XTAL1` instead of an SMD 
- Does not connately any 'no lead' packages (meaning it could be assembled with just a soldering iron, no hot air)

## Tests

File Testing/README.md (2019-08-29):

# Testing
### Power Switch

#### Switching Capacitive Load
The following is a breadboard test with an MIC2544 load switch, with a 1k&Omega; limit resistor (0.23A) switching 5v onto a discharged 680uF capacitor. The power supply which drives this circuit was set for 5v and 0.5A current limit (in order to prevent external limiting). In this capture we see the load switch limiting the current to the capacitor, increasing the rise time (to 12ms) and preventing problematic current draws onto the data logger. 
MIC2544 Capacitor Switch
* Red -> `EN`
* Yellow -> `FLG`
* Blue -> I<sub>In</sub> (10V/A)
* Green -> V<sub>Out</sub>

The following shows the same event, but a detailed view of the turn on event to illustrate the timing and current peak in more detail

MIC2544 Capacitor Switch
* Red -> `EN`
* Yellow -> `FLG`
* Blue -> I<sub>In</sub> (10V/A)
* Green -> V<sub>Out</sub>

##### v0.1 Update
Testing for v0.1 hardware (switched from MOSFET control to MIC2544 load switch with current limiting)

Inrush current with Margay v2.2 output rail used as power supply. R<sub>Lim</sub> = 2.2k&Omega; 
Note, initial inrush spike, then reduced current. Initial spike does not result in brown out of Margay. LiDAR Lite static current consumption is able to be supported by the Margay v2.2 external 3.3v rail.
v0.1 Power On, Margay Supply
* Yellow -> I<sub>In</sub> (10V/A)
* Blue -> V<sub>In</sub> 

This figure shows the same waveform as above, but a detailed view of the switching 
v0.1 Power On Detail, Margay Supply
* Yellow -> I<sub>In</sub> (10V/A)
* Blue -> V<sub>In</sub> 

This figure shows the risetime of the 5v switched rail on board the Symbiont board. In this case we see the rise time which is controlled by the limiting of the current from the MIC2544 switch (R<sub>Lim</sub> = 2.2k&Omega;)
v0.1 5v SW Rise Time, Margay Supply
* Red -> V<sub>5v_SW</sub>
* Blue -> V<sub>In</sub> 

The following shows the problem if the current limit is set too high (R<sub>Lim</sub> = 1.05k&Omega;), the core 5v rail sags (due to hitting the current limit of the boost converter), which causes the brown out detect to engage and lock the device into a perpetual reset state. After the reset is triggered due to the sag of the core voltage below 4.3v (brownout limit), we see oscillation occur and the device held in reset.
Excess current limit, Power Supply
* Red -> V<sub>5v_Core</sub>
* Yellow -> I<sub>In</sub>

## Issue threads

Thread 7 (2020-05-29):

### ISSUE TITLE
Which firmware is the default?

### ISSUE THREAD

**Issue by awickert** [NorthernWidget-Skunkworks/Project-Symbiont-LiDAR#7]
There are three currently. Could we either remove deprecated ones or create a "FirmwareTests" folder or a "tests" subfolder or something like this to distinguish?

**Comment by bschulz1701** [comment]
Sorry for the naming confusion, **`LiDAR_InterfaceDemo.ino`** should be the full functional firmware. `LiDAR_Accelerometer_InterfaceDemo.ino` does not have full control functionality for the LiDAR Lite or the hall effect sensor, and `HallEffect_Tester.ino` is simply a demo script to test magnet strength and area of effect most easily

**Comment by awickert** [comment]
* Renamed `LiDAR_InterfaceDemo.ino` to `LiDAR_Interface.ino`
* Moved the others to a subfolder with the notes provided here.

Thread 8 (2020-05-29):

### ISSUE TITLE
Which hardware is standard?

### ISSUE THREAD

**Issue by awickert** [NorthernWidget-Skunkworks/Project-Symbiont-LiDAR#8]
Several versions are listed; could deprecated ones be removed? I have created a v0.0.0 release, and they'll live on in that and in the git history.

**Comment by bschulz1701** [comment]
Standard hardware is `LiDAR_Lite_Interface_HardSwitch` the rest exist only as potential designs, but for reference, these are the variations in the designs (Note: **All designs except `LiDAR_Lite_Interface_HardSwitch` are untested!**

`LiDAR_Lite_Interface`
- Most minimal implementation
- Fixed I2C, no UART capability
- No accelerometer 

`LiDAR_Lite_Interface_CAN`
- Unfinished minor variant of `LiDAR_Lite_Interface`
- Uses can type crystal with tabs for `XTAL1` instead of an SMD 
- Does not connately any 'no lead' packages (meaning it could be assembled with just a soldering iron, no hot air)

 `LiDAR_Lite_Interface_HardSwitch`
- A expanded version of `LiDAR_Lite_Interface`
- Adds accelerometer 
- Uses physical switch to toggle between UART and I2C communication (as opposed to being firmware controlled in `LiDAR_Lite_Interface` and `LiDAR_Lite_Interface_CAN`
- Adds power switch to disconnect LiDAR Lite 
- Adds hall effect switch to trigger auto-level or other operation

**Comment by awickert** [comment]
Untested designs moved to subdirectories and READMEs added as direct copy/paste from text provided here.

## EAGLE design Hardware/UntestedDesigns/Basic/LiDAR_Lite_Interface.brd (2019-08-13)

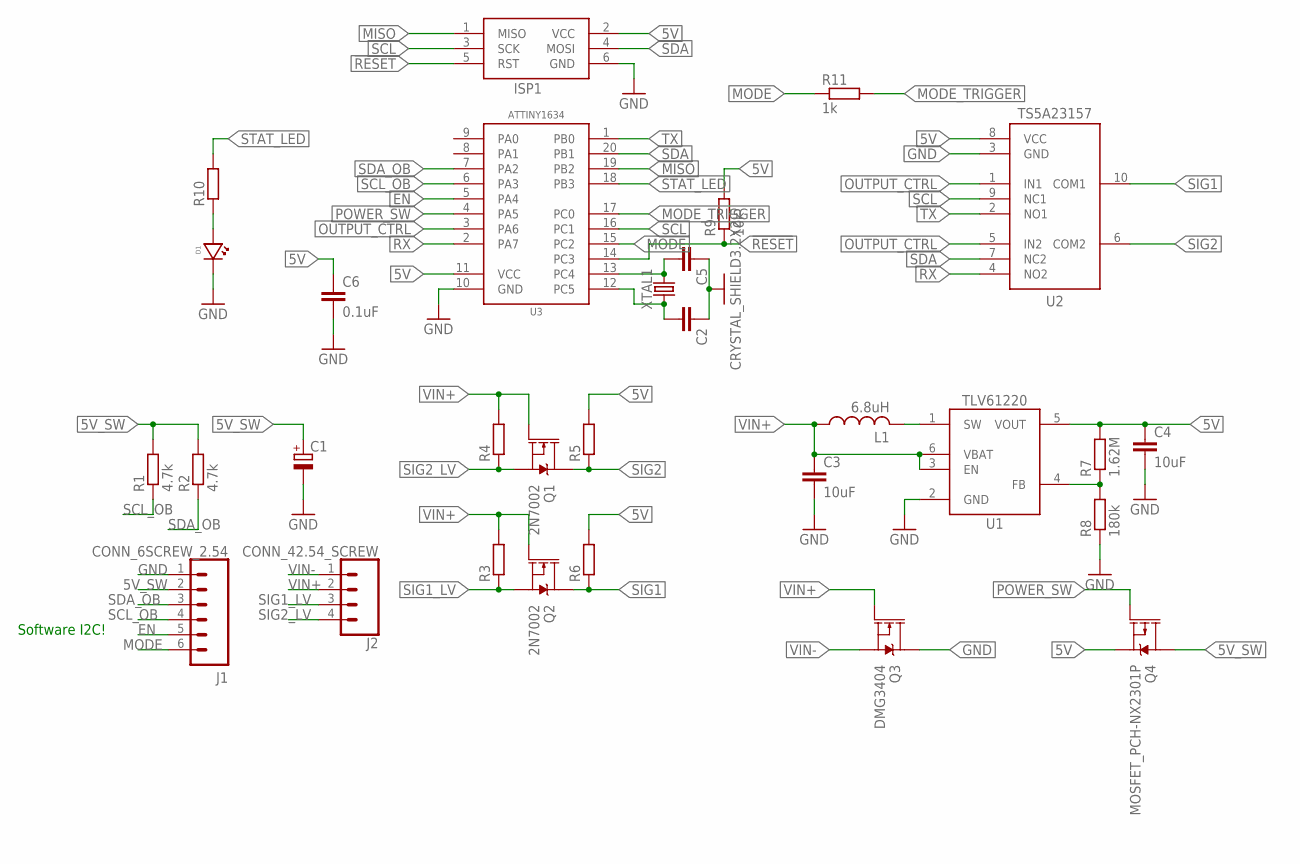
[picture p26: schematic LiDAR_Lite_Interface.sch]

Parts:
C1: CPOL-EUUW-10X10; UW-10X10_NICHICON
C2, C5: C-EU10PFC0603; C0603
C3, C4: 10uF; C0805
C6: 0.1uF; C0603
D1: LED0603; LED_0603
ISP1: AVRISP-6; AVRISP
J1: CONN_6SCREW_2.54; 1X06_SCREW
J2: CONN_42.54_SCREW; 1X04_SCREW
L1: 6.8uH; 1008; MPN 74438323068; DIGIKEY 732-4849-1-ND
Q1, Q2: 2N7002; SOT23-3
Q3: DMG3404; SOT23-3
Q4: MOSFET_PCH-NX2301P; SOT23-3
R1, R2: 4.7k; R0603
R3, R4, R5, R6: R-EU_10KR0603; R0603
R7: 1.62M; R0603
R8: 180k; R0603
R9: 10k; R0603
R10: R-EU_330R0603; R0603
R11: 1k; R0603
U1: TLV61220DBV; DBV_R-PDSO-G6
U2: TS5A23157DGS; DGS0010A
U3: ATTINY1634SOIC; SO-20DW
XTAL1: CRYSTAL_SHIELD3.2X2.5; CRYSTAL_3.2X2.5_4-SMD; MPN ABM8G-12.000MHZ-4Y-T3; DIGIKEY 535-10901-1-ND

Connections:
5V: C4.1, C6.1, ISP1.2 (VCC), Q4.2 (S), R5.2, R6.2, R7.2, R9.2, U1.5 (VOUT), U2.8 (VCC), U3.11 (VCC)
5V_SW: C1.+, J1.2, Q4.3 (D), R1.2, R2.2
!RESET: ISP1.5 (RST), R9.1, U3.14 (PC3)
EN: J1.5, U3.5 (PA4)
GND: C1.-, C2.1, C3.2, C4.2, C5.1, C6.2, D1.CATHODE, ISP1.6 (GND), J1.1, Q3.3 (D), R8.1, U1.2 (GND), U2.3 (GND), U3.10 (GND), XTAL1.2 (GND), XTAL1.4 (GND)
MISO: ISP1.1 (MISO), U3.19 (PB2)
MODE: J1.6, R11.1, U3.15 (PC2)
MODE_TRIGGER: R11.2, U3.17 (PC0)
unnamed: C5.2, U3.13 (PC4), XTAL1.3 (2)
unnamed: C2.2, U3.12 (PC5), XTAL1.1
unnamed: D1.ANODE, R10.1
unnamed: R7.1, R8.2, U1.4 (FB)
unnamed: L1.2, U1.1 (SW)
OUTPUT_CTRL: U2.1 (IN1), U2.5 (IN2), U3.3 (PA6)
POWER_SW: Q4.1 (G), U3.4 (PA5)
RX: U2.4 (NO2), U3.2 (PA7)
SCL: ISP1.3 (SCK), U2.9 (NC1), U3.16 (PC1)
SCL_OB: J1.4, R1.1, U3.6 (PA3)
SDA: ISP1.4 (MOSI), U2.7 (NC2), U3.20 (PB1)
SDA_OB: J1.3, R2.1, U3.7 (PA2)
SIG1: Q2.3 (D), R6.1, U2.10 (COM1)
SIG1_LV: J2.3, Q2.2 (S), R3.1
SIG2: Q1.3 (D), R5.1, U2.6 (COM2)
SIG2_LV: J2.4, Q1.2 (S), R4.1
STAT_LED: R10.2, U3.18 (PB3)
TX: U2.2 (NO1), U3.1 (PB0)
VIN+: C3.1, J2.2, L1.1, Q1.1 (G), Q2.1 (G), Q3.1 (G), R3.2, R4.2, U1.3 (EN), U1.6 (VBAT)
VIN-: J2.1, Q3.2 (S)

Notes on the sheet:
Software I2C!

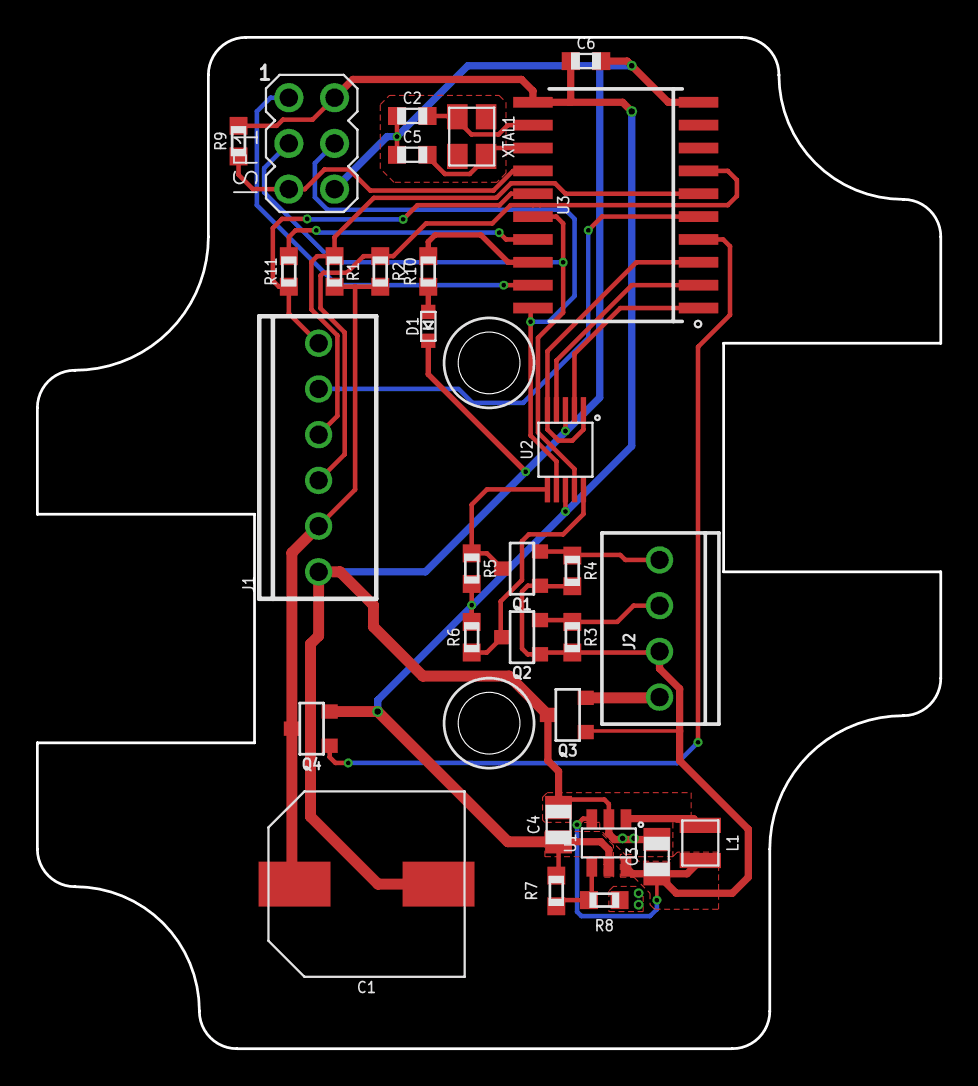
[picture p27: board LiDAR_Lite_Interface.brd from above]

Board: 2 copper layers, 50.2 x 56.2 mm, 30 parts (0 on the bottom side), 28 nets.

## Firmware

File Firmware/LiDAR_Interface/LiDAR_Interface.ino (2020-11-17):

//Dyson_Driver_ShortWave.ino
#include "SlowSoftI2CMaster.h"
#include "WireS.h"
#include <avr/sleep.h>
#include <EEPROM.h>
// #include <EEPROM.h> //DEBUG!
//Commands
#define CTRL_REG1_ADR 0x20
#define CTRL_REG2_ADR 0x21
#define CTRL_REG3_ADR 0x22
#define CTRL_REG4_ADR 0x23
#define TEMP_CFG_REG_ADR 0x1F
#define OUT_X_ADR 0x28 //Low byte
#define OUT_Y_ADR 0x2A
#define OUT_Z_ADR 0x2C

#define POWER_SW 2

#define ACCEL_INT 7 //Interrupt from accelerometer, active low, needs internal pullup
#define MODE_TRIGGER 13 //Trigger for pulse width mode
#define MODE_READ 11 //Read pin for pulse width mode, also INTO
#define STAT_LED 14 //Status LED
#define HALL_SWITCH 8 //Hall effect switch output 
#define ENABLE 4 //Enable pin for Lidar Lite


// #define ACCEL_ADR 0x18
const int ACCEL_ADR = 0x18; //DEBUG!

#define LIDAR_ADR 0x62

#define READ 0x01
#define WRITE 0x00

#define BUF_LENABLEGTH 64 //Length of I2C Buffer, verify with documentation 

// #define ADR_ALT 0x41 //Alternative device address

const unsigned long GlobalTimeout = 200; //Time to wait before timing out

bool LidarFail = false; //Used to indicate failure of Lidar unit
bool AccelFail = false; //Used to indicate failure of on board accelerometer 

volatile uint8_t ADR = 0x50; //Use arbitraty address, change using generall call??
// const uint8_t ADR_Alt = 0x41; //Alternative device address  //WARNING! When a #define is used instead, problems are caused

unsigned int Config = 0; //Global config value
unsigned long Period = 100; //Number of ms between sample events for continuious running

uint8_t Reg[16] = {0}; //Initialize registers
// bool StartSample = true; //Flag used to start a new converstion, make a conversion on startup
// const unsigned int UpdateRate = 5; //Rate of update

SlowSoftI2CMaster si = SlowSoftI2CMaster(PIN_A2, PIN_A3, true);  //Initialize software I2C

volatile bool StopFlag = false; //Used to indicate a stop condition 
volatile uint8_t RegID = 0; //Used to denote which register will be read from
volatile bool RepeatedStart = false; //Used to show if the start was repeated or not

int16_t Offsets[3] = {0};  //X,Y,Z acceleration offsets to zero the angle of the device 
int16_t AccelVals[3] = {0}; //Global storage for acceleration data values to be shared between EEPROM functions and getter functions 

bool SwitchLatch = false;  //Latching functionality control for Hall effect switch 
uint8_t LiDAR_Config = 0; //Use default config 

void setup() {
  // Serial.begin(115200); //DEBUG!
  // Serial.println("begin"); //DEBUG!
  // pinMode(ADR_SEL_PIN, INPUT_PULLUP);
  // if(!digitalRead(ADR_SEL_PIN)) ADR = ADR_Alt; //If solder jumper is bridged, use alternate address //DEBUG!
  pinMode(STAT_LED, OUTPUT);
  digitalWrite(STAT_LED, HIGH);
  pinMode(POWER_SW, OUTPUT);
  // digitalWrite(POWER_SW, HIGH); //Turn on power //DEBUG!
  // delay(500); //DEBUG!
  digitalWrite(POWER_SW, LOW); //Turn off output power //FIX??
  Wire.begin(ADR);  //Begin slave I2C
  Serial.begin(9600);
  // Serial.println("START"); //DEBUG!
  // EEPROM.write(0, ADR);

  //Setup I2C slave
  Wire.onAddrReceive(addressEvent); // register event
  Wire.onRequest(requestEvent);     // register event
  Wire.onReceive(receiveEvent);
  Wire.onStop(stopEvent);

  
  pinMode(ACCEL_INT, INPUT); //DEBUG! 
  pinMode(MODE_READ, INPUT);
  pinMode(MODE_TRIGGER, OUTPUT);
  pinMode(HALL_SWITCH, INPUT); 
  pinMode(ENABLE, OUTPUT);
  digitalWrite(ENABLE, LOW);
  digitalWrite(MODE_TRIGGER, HIGH); //Configure as pullup

  delay(10);
  digitalWrite(POWER_SW, HIGH); //Turn on power
  delay(100); //DEBUG!
  digitalWrite(ENABLE, HIGH);
  si.i2c_init(); //Begin I2C master
  InitAccel();
  InitLiDAR();
  digitalWrite(STAT_LED, LOW);  //Blink on statup
  if(!digitalRead(HALL_SWITCH)) {
    UpdateOffset(Offsets); //Clear values (offsets are 0 on startup until read into)
    SwitchLatch = true; //Set latch to prevent override 
  }
  digitalWrite(STAT_LED, HIGH);

}

void loop() {
  // static unsigned int Count = 0; //Counter to determine update rate
  // if(StartSample == true) {
  //  //Read new values in
  //  AutoRange_Vis();  //Run auto range
  //  delay(800); //Wait for new sample
  //  SplitAndLoad(0x0B, GetALS()); //Load ALS value
  //  SplitAndLoad(0x0D, GetWhite()); //Load white value
  //  SplitAndLoad(0x02, long(GetUV(0))); //Load UVA
  //  SplitAndLoad(0x07, long(GetUV(1))); //Load UVB
  //  SplitAndLoad(0x10, GetLuxGain()); //Load lux multiplier 
  //  SplitAndLoad(0x13, GetADC(0));
  //  SplitAndLoad(0x15, GetADC(1));
  //  SplitAndLoad(0x17, GetADC(2));

  //  StartSample = false; //Clear flag when new values updated  
  // }
  // if(Count++ == UpdateRate) {  //Fix update method??
  //  StartSample = true; //Set flag if number of updates have rolled over 
  //  Count = 0;
  // }

  // for(int i = 0; i < 128; i++) {
  //  si.i2c_start((i << 1) | WRITE);
  //  Serial.print(i, HEX);
  //  Serial.print('\t');
  //  Serial.println(si.i2c_write(0xFF)); //Write MSB
  //  si.i2c_stop();
  // }
  // while(digitalRead(7), LOW); //Wait for updated values //DEBUG!
  // ReadByte(ACCEL_ADR, 0x27);
  // ReadWord(ACCEL_ADR, OUT_X_ADR);
  LiDAR_Config = Reg[1] & 0x03; //Pull low two bits from Config reg 1 to get Lidar configuration state 
  InitLiDAR(); //reinitialize LiDAR after power cycle 
  unsigned long StartTime = millis();  //Measure time from start of measurment 
  uint8_t Stat1 = ReadByte(ACCEL_ADR, 0x27); 
  uint8_t Stat2 = ReadByte(ACCEL_ADR, 0x07);
  // while(((Stat1 & 0x08) >> 3) != 1 || ((Stat2 & 0x08) >> 3) != 1 || ((Stat2 & 0x80) >> 7) != 1) {
  unsigned long LocalTime = millis();
  while(((Stat1 & 0x08) >> 3) != 1 || Stat2 != 0xFF && (millis() - LocalTime) < GlobalTimeout) {  //Try to get status from 
    Stat1 = ReadByte(ACCEL_ADR, 0x27);
    Stat2 = ReadByte(ACCEL_ADR, 0x07);
    delay(1); //DEBUG!
  }
  if((millis() - LocalTime) < GlobalTimeout) AccelFail = true; //Set flag if timeout occoured 
  else AccelFail = false;

  // si.i2c_read(false);
  // si.i2c_read(false);
  // si.i2c_read(false); //DEBUG!
  // si.i2c_read(false);
  // si.i2c_read(false);
  delay(5); //DEBUG!
  // while(((ReadByte(ACCEL_ADR, 0x27) & 0x08) >> 3) != 1 || (digitalRead(7) == LOW)); //Wait for updated values

  // Serial.println("START"); //DEBUG!
  // Serial.println(Stat1, BIN); //DEBUG! 
  // Serial.println(Stat2, BIN); //DEBUG!
  // Serial.print("\n\n"); //Newline return

  int16_t Range = GetRange();  //DEBUG! Replace!
  Serial.print('R'); //Preceed range value
  Serial.println(Range); 

  digitalWrite(ENABLE, LOW);
  digitalWrite(POWER_SW, LOW); //Turn off 5v switched power
  GetOffsets(); //Read in offsets
  GetG(true);
  // Serial.println(ReadByte(LIDAR_ADR, 0x0E)); //DEBUG! //READ RSSI

  // for(int i = 0; i < 3; i++) {
  //  Serial.println(GetG(i));
  // }
  // Serial.println(ReadByte(ACCEL_ADR, 0x27), BIN); //DEBUG! 
  
  // delay(1000);
  while((millis() - StartTime) < Period) {  //Wait for period rollover 
    set_sleep_mode(SLEEP_MODE_IDLE);   // sleep mode is set here
    sleep_enable();
    sei();
    sleep_cpu();
    

    if(!digitalRead(HALL_SWITCH) && !SwitchLatch) {  //Only run update if switch is not lauched previously (new application of trigger)
      SwitchLatch = true; //latch switch until toggle of state
      digitalWrite(STAT_LED, HIGH); //Turn on status LED while latched 
      GetG(false); //Get new acclerometer values
      UpdateOffset(AccelVals);
    }
    if(digitalRead(HALL_SWITCH)) {
      SwitchLatch = false; //If switch is high, back to default state, reset latch 
      digitalWrite(STAT_LED, LOW); //Turn off stat LED once latch is cleared 
    }
    // if(Serial.available() > 0) {  //FIX add serial control??
    //  uint8_t Data1 = Serial.read();
    //  uint8_t Data2 = Serial.read();
    //  if(Data2 == 'F') Ctrl = Data1; //If 
    // }
  }
  sleep_disable();
  digitalWrite(POWER_SW, HIGH); //Turn on 5v switched power
  delay(100); //Wait for voltage to stabilize after cap charge 
  digitalWrite(ENABLE, HIGH); //NOTE: MUST toggle enable after voltage ramp to ensure effective measurment 
  // while(Serial.available() < 1 && digitalRead())
}

// float GetAngle(uint8_t Axis)
// {
//  float ValX = GetG(0); //Used to get g values
//  float ValY = GetG(1);
//  float ValZ = GetG(2);
//   float Val = 0;
//   switch(Axis) {
//     case(0):
//       Val = asin(ValX); 
//       break;
//     case(1):
//       Val = asin(ValY);
//       break;
//     case(2):
//       Val = acos(ValZ);
//       break;
//     case(3):
//       Val = atan(ValX/(sqrt(pow(ValY, 2) + pow(ValZ, 2))))*(180.0/3.14); //Return pitch angle
//       break;
//     case(4):
//       Val = atan(ValY/(sqrt(pow(ValX, 2) + pow(ValZ, 2))))*(180.0/3.14); //Return roll angle
//       break;
//   }
//   if(ValX == ValY && ValX == ValZ) Val = -9999; //Return error value is all vals are the same (1 in 6.87x10^10 likelyhood of occouring without error)
//   return Val; 
// }

uint8_t InitAccel() 
{
  // WriteByte(ACCEL_ADR, CTRL_REG1_ADR, 0x07);
  WriteByte(ACCEL_ADR, CTRL_REG1_ADR, 0x77); //Set for 100Hz output data rate //FIX! Set to low power initally??
  WriteByte(ACCEL_ADR, CTRL_REG4_ADR, 0x88); //Turn on high resolution mode //FIX! Setup to use self text
  WriteByte(ACCEL_ADR, CTRL_REG3_ADR, 0x10);
  WriteByte(ACCEL_ADR, TEMP_CFG_REG_ADR, 0x80);
}

float GetG(bool Set)  //FIX! Add offset support //By default set/send data to registers 
{ 
  // uint8_t AxisADR = OUT_X_ADR + 2*Axis; //Add appropriate offset
  // int16_t Data = ReadWord(ACCEL_ADR, AxisADR);
  // return Data*(4.0/4096.0); //FIX! Make fixed integer! 
  // Command |= 0x80; //turn on auto increment //FIX!!! Remove for other I2C transactions 
  bool OutOfRange = false; //Used to test if values are within expected range
  int16_t Axis[3] = {0}; //Initalize variables for x,y,z values

  bool Error = SendCommand(ACCEL_ADR, OUT_X_ADR | 0x80);
  si.i2c_stop(); 

  uint8_t Data[6] = {0}; //Init data
  si.i2c_start((ACCEL_ADR << 1) | READ);
  for(int i = 0; i < 6; i++) {
    Data[i] = si.i2c_read(false);
  }
  si.i2c_stop();
  for(int i = 0; i < 3; i++) {
    Axis[i] = (((int16_t)(Data[2*i + 1] << 8) | (int16_t)Data[2*i]) >> 4);
  }

  if(Error == false || OutOfRange) {  //If read error occours 
    AccelFail = true; //Set flag
    Axis[0] = -9999;
    Axis[1] = -9999;
    Axis[2] = -9999;
  }
  else {  //Otherwise load/send data normally 
    AccelFail = false; //Clear flag
    for(int i = 0; i < 3; i++) AccelVals[i] = Axis[i]; //Copy local raw axis data to accel vals

    if(Set) {  //If sending data is commanded, print data out
      Serial.print('X'); Serial.println(Axis[0] - Offsets[0]);  //FIX! Optimize to prevent multiple addition 
      Serial.print('Y'); Serial.println(Axis[1] - Offsets[1]);
      Serial.print('Z'); Serial.println(Axis[2] - Offsets[2]);

      SplitAndLoad(0x04, Axis[0]);  //Load accel values
      SplitAndLoad(0x06, Axis[1]);
      SplitAndLoad(0x08, Axis[2]);

      SplitAndLoad(0x0A, Offsets[0]);  //Load offsets
      SplitAndLoad(0x0C, Offsets[1]);
      SplitAndLoad(0x0E, Offsets[2]);
    }
  }


  // return Data;
}
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

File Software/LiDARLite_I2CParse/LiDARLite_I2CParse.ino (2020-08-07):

#include <Margay.h>

String Header = ""; //Information header
uint8_t I2CVals[1] = {0x50};
unsigned long UpdateRate = 300; //Number of seconds between readings

Margay Logger(Model_2v0);

void setup() {
	Header = Header + "Range [cm], Pitch [deg], Roll [deg]";
	Logger.begin(I2CVals, sizeof(I2CVals), Header); //Pass header info to logger
	Init();
}

void loop() {
	Logger.Run(Update, UpdateRate);

}

String Update()
{
	Init();
	// delay(1000); //DEBUG!
	delay(200);
	return ReadI2CData();
}

void Init()
{
	Wire.begin();
	Wire.beginTransmission(0x50);
	Wire.write(0x01);
	Wire.write(0x00); //Set for high sensitivity
	Wire.endTransmission();
}


String ReadI2CData()
{
	const unsigned long Timeout = 200; //Wait up to 200ms for a new reading
	unsigned long LocalTime = millis(); //Keep track of local time for timeout

	uint8_t Data1 = 0;
	uint8_t Data2 = 0;
	uint8_t ADR = 0x50; //FIX! Make global const!

	int16_t DataSet[7] = {0}; //Used to store set of data read in from I2C

	for(int i = 0; i < 7; i++) {
		Wire.beginTransmission(ADR);
		Wire.write(2*i + 2);
		Wire.endTransmission();
		Wire.requestFrom(ADR, 1);
		Data1 = Wire.read();

		Wire.beginTransmission(ADR);
		Wire.write(2*i + 3);
		Wire.endTransmission();
		Wire.requestFrom(ADR, 1);
		Data2 = Wire.read();

		DataSet[i] = ((Data2 << 8) | Data1); //Store data in array
	}

  // Takes up memory but makes code easier to read. Could be more efficient.
  // Perhaps use pointers, or just comments?
  float Range = DataSet[0]

  // Convert g vals to floats for math
	float ValX = DataSet[1];
	float ValY = DataSet[2];
	float ValZ = DataSet[3];

	float OffsetX = DataSet[4];
	float OffsetY = DataSet[5];
	float OffsetZ = DataSet[6];

	float Pitch = 0;
	float Roll = 0;

	if(OffsetX == OffsetY && OffsetX == OffsetZ && OffsetX == 0) {  //Do not include angle calc for offset when offset is 0 (Results in NAN value)
		// Pitch = atan(-ValX/(sqrt(pow(ValY, 2) + pow(ValZ, 2))))*(180.0/3.14);
		Pitch = atan(-ValX/ValZ)*(180.0/3.14);
		Roll = atan(ValY/(sqrt(pow(ValX, 2) + pow(ValZ, 2))))*(180.0/3.14);
	}
	else {
		// Pitch = atan(-ValX/(sqrt(pow(ValY, 2) + pow(ValZ, 2))))*(180.0/3.14) - (atan(-OffsetX/(sqrt(pow(OffsetY, 2) + pow(OffsetZ, 2))))*(180.0/3.14));
		Pitch = atan(-ValX/ValZ)*(180.0/3.14) - (atan(-OffsetX/OffsetZ)*(180.0/3.14));
		Roll = atan(ValY/(sqrt(pow(ValX, 2) + pow(ValZ, 2))))*(180.0/3.14) - (atan(OffsetY/(sqrt(pow(OffsetX, 2) + pow(OffsetZ, 2))))*(180.0/3.14));
	}

	if(DataSet[0] < 0) DataSet[0] = -9999; //Check for invalid range
	if(DataSet[1] == DataSet[2] && DataSet[1] == DataSet[3] && DataSet[1] == -1) {  //If all values are -1 set pitch and roll out of range
		Pitch = -9999;
		Roll = -9999;
	}


	// return String(DataSet[0]) + "," + String(DataSet[1]) + "," + String(DataSet[2]) + "," + String(DataSet[3]) + ",";
	return String(DataSet[0]) + "," + String(Pitch) + "," + String(Roll) + ",";
}

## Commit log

2019-07-11 Preliminary design and layout
    Very minimal layout, first round of schematic design
    [LiDAR_Lite_Interface.brd, LiDAR_Lite_Interface.sch]
2019-07-13 Updated layout, added variants
    Improved layout, potentially add button, then ready to send to fab. Added variations of layout for potential future alteration
    [LiDAR_Lite_Interface_CAN.brd, LiDAR_Lite_Interface_CAN.sch, LiDAR_Lite_Interface_HardSwitch.brd, LiDAR_Lite_Interface_HardSwitch.sch]
2019-07-15 Added accel and hall effect, sent to fab
    Updated layout, added accelerometer, hall effect switch, generated gerbers and sent to fab
    [LiDAR_Lite_Interface_HardSwitch.brd, LiDAR_Lite_Interface_HardSwitch.sch]
2019-07-26 Minor value updates, generated BoM
    [LiDAR_Lite_Interface_HardSwitch.brd, LiDAR_Lite_Interface_HardSwitch.csv, LiDAR_Lite_Interface_HardSwitch.sch]
2019-08-10 Minor adjustments to firmware test
    Added light blink on startup, changed power sequence to reduce brownout risk
2019-08-13 Design updates and gerbers, final DFM required
    Added Gerbers for OSH park, naming update, pending v0.2 design
    [LiDAR_Lite_Interface.brd, LiDAR_Lite_Interface.sch, LiDAR_Lite_Interface_CAN.brd, LiDAR_Lite_Interface_CAN.sch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]
2019-08-13 Firmware updates, added hardware testing documentation
    [LiDAR_Lite_Interface_HardSwitch.csv]
2019-08-14 Minor edits, changed external LED topology, sent v0.1 to fab
    Changed external LED to use independent resistor, generated gerbers, sent v0.1 to fab
    [LiDAR_Lite_Interface_HardSwitch.brd, LiDAR_Lite_Interface_HardSwitch.sch]
2019-08-15 Added board shape drawing
2019-08-29 Updated BoM for v0.1
    [LiDAR_Lite_Interface_HardSwitch.csv]
2019-09-05 Added I2C and serial parsing sketches
    Added sketches to serve as basis for library for device
2019-09-05 Performance updates to firmware demo
    Changed update time, removed START print due to causing problems with parsing serial output values, fixed random 0 output issue by forcing the on board I2C bus to be released after getting data from 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
    Documentation and clean up still needed
2020-04-30 Physical hardware and mounts
    [LiDARLiteCover.SLDPRT, LiDARLiteCover.STL, LiDARLite_Symbiont.SLDPRT, LiDARLite_Symbiont_Mount.DXF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]
2020-05-04 Mounting plate, "safety glasses", magnet level offset
2020-05-07 Correct to "sensor"
2020-05-25 @bschulz1701 advice: ISP power, mounting plate, hole+tap size
    Former-commit-id: 05432e0b7ff8a9273416ca4c78c0727f79e6abba
2020-05-25 Symbiont mount render
2020-05-27 U bolt dimensions for mounting plate
2020-05-27 Black acetal (UV); 1 1/8" U bolts for 3/4" pipe
2020-05-29 No leadless packages: can be hand soldered
    [LiDAR_Lite_Interface_CAN.brd, LiDAR_Lite_Interface_CAN.sch]
2020-05-29 Most basic board: initial design
    [LiDAR_Lite_Interface.brd, LiDAR_Lite_Interface.sch]
2020-05-31 Make status LED flash patterns: now issue #13
2020-05-31 Inline note to Issue #14: power consumption from lab notebook
2020-08-10 Input range 3.3V to 5.5V
2020-08-24 3/8" sealing screw? M10 hole/tap?
2020-09-03 Update sealing screws and link to 3/8"
2021-04-08 Updated assembly instructions
    bootloading, I2C, desiccant placement
2021-04-08 Hall Effect sensor labeled
2021-07-13 Cables >3 m not sure to work (I2C)
2024-09-19 Added box mechanical designs and drawings
    [90825A142_Sealing Pan Head Screws.SLDPRT, 97349A415_Rounded Head Thread-Forming Screws.SLDPRT, 99022A101_18-8 Stainless Steel Cap Nut.SLDPRT, Full.SLDASM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]
2024-09-19 Updated README with assembly render
2024-09-19 Added STEP files of milled box parts
    [WC-20F_Body.STEP, WC-20F_Lid.STEP]
2024-09-27 Added box printing template
2024-11-02 Added documentation and mechanical design/render
    [7310K51_Plastic Submersible Cord Grip_NONUT.SLDPRT, 90825A162_Sealing Pan Head Screws.SLDPRT, 91855A430_18-8 Stainless Steel Cap Nut.SLDPRT, LiDAR_Lite_Interfa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]

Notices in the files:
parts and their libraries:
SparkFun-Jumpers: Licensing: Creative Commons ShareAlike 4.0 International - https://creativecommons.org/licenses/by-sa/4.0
